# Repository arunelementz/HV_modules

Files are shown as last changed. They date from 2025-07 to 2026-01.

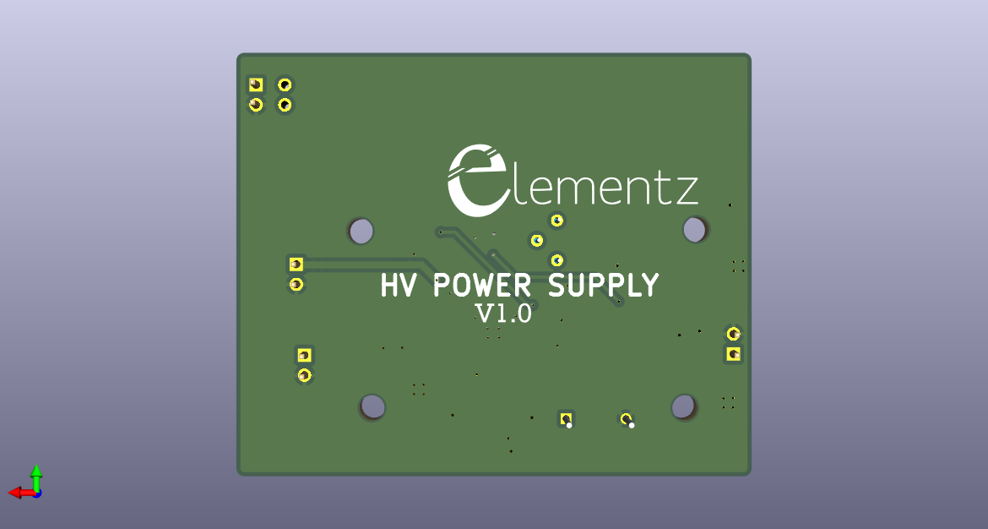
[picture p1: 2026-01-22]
PCB_Design/HV_POWER_SUPPLY_newshape/HV_POWER_SUPPLY_NEWSHAPE_bottom_new.png

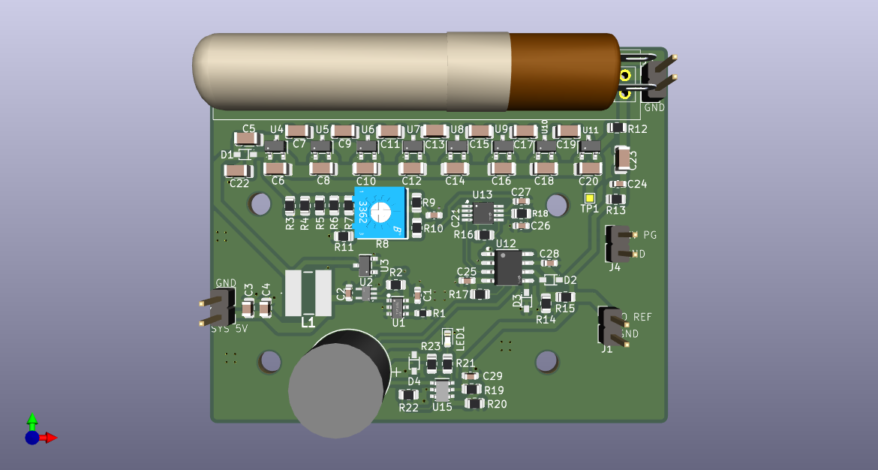
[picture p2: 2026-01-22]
PCB_Design/HV_POWER_SUPPLY_newshape/HV_POWER_SUPPLY_NEWSHAPE_top_new.png

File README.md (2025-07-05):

# HV_Module for GM tubes

## Getting started

To make it easy for you to get started with GitLab, here's a list of recommended next steps.

Already a pro? Just edit this README.md and make it your own. Want to make it easy? [Use the template at the bottom](#editing-this-readme)!

## Add your files

- [ ] [Create](https://docs.gitlab.com/ee/user/project/repository/web_editor.html#create-a-file) or [upload](https://docs.gitlab.com/ee/user/project/repository/web_editor.html#upload-a-file) files
- [ ] [Add files using the command line](https://docs.gitlab.com/topics/git/add_files/#add-files-to-a-git-repository) or push an existing Git repository with the following command:

```
cd existing_repo
git remote add origin https://gitlab.com/arunelementz/hv_module-for-gm-tubes.git
git branch -M main
git push -uf origin main
```

## Integrate with your tools

- [ ] [Set up project integrations](https://gitlab.com/arunelementz/hv_module-for-gm-tubes/-/settings/integrations)

## Collaborate with your team

- [ ] [Invite team members and collaborators](https://docs.gitlab.com/ee/user/project/members/)
- [ ] [Create a new merge request](https://docs.gitlab.com/ee/user/project/merge_requests/creating_merge_requests.html)
- [ ] [Automatically close issues from merge requests](https://docs.gitlab.com/ee/user/project/issues/managing_issues.html#closing-issues-automatically)
- [ ] [Enable merge request approvals](https://docs.gitlab.com/ee/user/project/merge_requests/approvals/)
- [ ] [Set auto-merge](https://docs.gitlab.com/user/project/merge_requests/auto_merge/)

## Test and Deploy

Use the built-in continuous integration in GitLab.

- [ ] [Get started with GitLab CI/CD](https://docs.gitlab.com/ee/ci/quick_start/)
- [ ] [Analyze your code for known vulnerabilities with Static Application Security Testing (SAST)](https://docs.gitlab.com/ee/user/application_security/sast/)
- [ ] [Deploy to Kubernetes, Amazon EC2, or Amazon ECS using Auto Deploy](https://docs.gitlab.com/ee/topics/autodevops/requirements.html)
- [ ] [Use pull-based deployments for improved Kubernetes management](https://docs.gitlab.com/ee/user/clusters/agent/)
- [ ] [Set up protected environments](https://docs.gitlab.com/ee/ci/environments/protected_environments.html)

***

# Editing this README

When you're ready to make this README your own, just edit this file and use the handy template below (or feel free to structure it however you want - this is just a starting point!). Thanks to [makeareadme.com](https://www.makeareadme.com/) for this template.

## Suggestions for a good README

Every project is different, so consider which of these sections apply to yours. The sections used in the template are suggestions for most open source projects. Also keep in mind that while a README can be too long and detailed, too long is better than too short. If you think your README is too long, consider utilizing another form of documentation rather than cutting out information.

## Name
Choose a self-explaining name for your project.

## Description
Let people know what your project can do specifically. Provide context and add a link to any reference visitors might be unfamiliar with. A list of Features or a Background subsection can also be added here. If there are alternatives to your project, this is a good place to list differentiating factors.

## Badges
On some READMEs, you may see small images that convey metadata, such as whether or not all the tests are passing for the project. You can use Shields to add some to your README. Many services also have instructions for adding a badge.

## Visuals
Depending on what you are making, it can be a good idea to include screenshots or even a video (you'll frequently see GIFs rather than actual videos). Tools like ttygif can help, but check out Asciinema for a more sophisticated method.

## Installation
Within a particular ecosystem, there may be a common way of installing things, such as using Yarn, NuGet, or Homebrew. However, consider the possibility that whoever is reading your README is a novice and would like more guidance. Listing specific steps helps remove ambiguity and gets people to using your project as quickly as possible. If it only runs in a specific context like a particular programming language version or operating system or has dependencies that have to be installed manually, also add a Requirements subsection.

## Usage
Use examples liberally, and show the expected output if you can. It's helpful to have inline the smallest example of usage that you can demonstrate, while providing links to more sophisticated examples if they are too long to reasonably include in the README.

## Support
Tell people where they can go to for help. It can be any combination of an issue tracker, a chat room, an email address, etc.

## Roadmap
If you have ideas for releases in the future, it is a good idea to list them in the README.

## Contributing
State if you are open to contributions and what your requirements are for accepting them.

For people who want to make changes to your project, it's helpful to have some documentation on how to get started. Perhaps there is a script that they should run or some environment variables that they need to set. Make these steps explicit. These instructions could also be useful to your future self.

You can also document commands to lint the code or run tests. These steps help to ensure high code quality and reduce the likelihood that the changes inadvertently break something. Having instructions for running tests is especially helpful if it requires external setup, such as starting a Selenium server for testing in a browser.

## Authors and acknowledgment
Show your appreciation to those who have contributed to the project.

## License
For open source projects, say how it is licensed.

## Project status
If you have run out of energy or time for your project, put a note at the top of the README saying that development has slowed down or stopped completely. Someone may choose to fork your project or volunteer to step in as a maintainer or owner, allowing your project to keep going. You can also make an explicit request for maintainers.

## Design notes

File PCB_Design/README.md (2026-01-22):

## HV Schematic and PCB Design Notes

- Schematic is the same as the original **CN0536 board**, including all annotations.
- **Sound notification** is **not included** in the PCB design.
- **BOM** is based on the original **CN0536 BOM**.
- **R19 and R20** are changed to **30 MΩ**  
  - Note: CN0536 BOM specifies **30 MΩ**, but a **different value appears in the schematic** and needs verification.
- **CN0536 stack arrangement** differs and should follow the reference shown.

- **Footprints to be confirmed**:
  - L1  
  - R9  
  - U1  
  - U5
- **Edge cuts** and **high-voltage trace clearance** need to be confirmed.
- **Potentiometer pin numbering** in schematic symbols has been checked.
- **Polygons** are used for drawing copper zones.

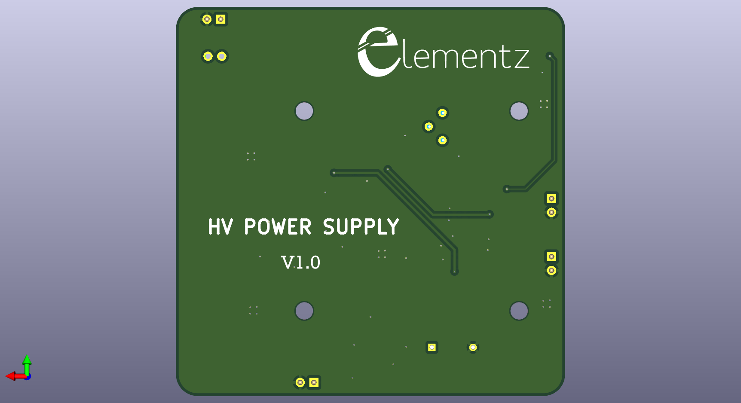
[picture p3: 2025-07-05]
PCB_Design/HV_POWER_SUPPLY_newshape/HV_POWER_SUPPLY_NEWSHAPE_bottom_view.png

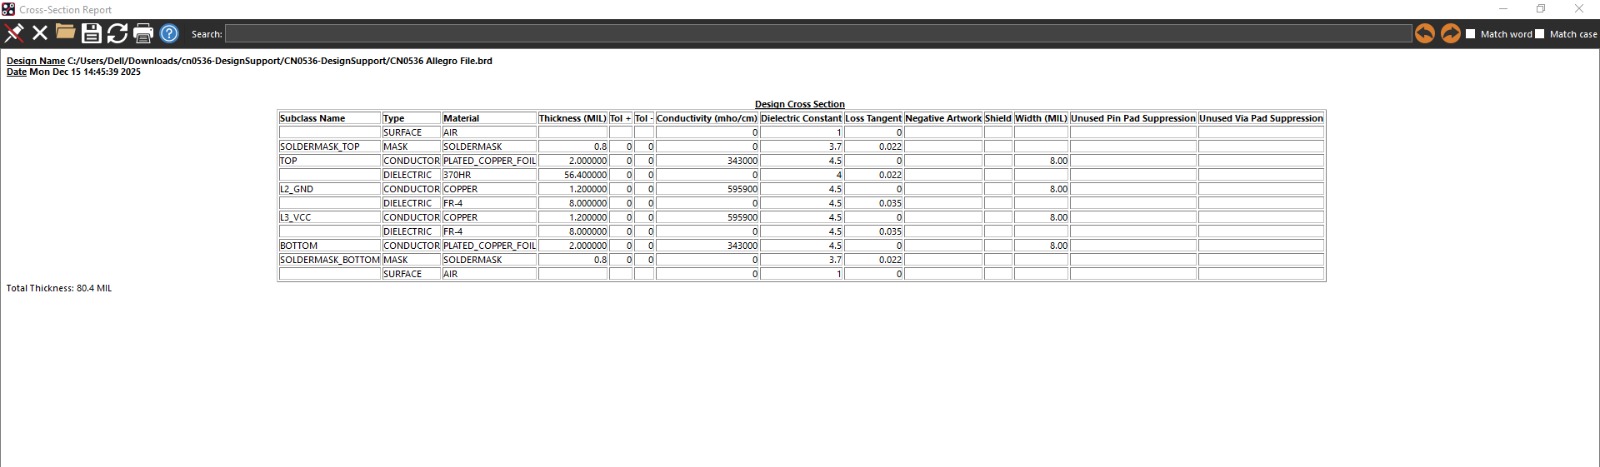
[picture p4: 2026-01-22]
PCB_Design/Stack.png

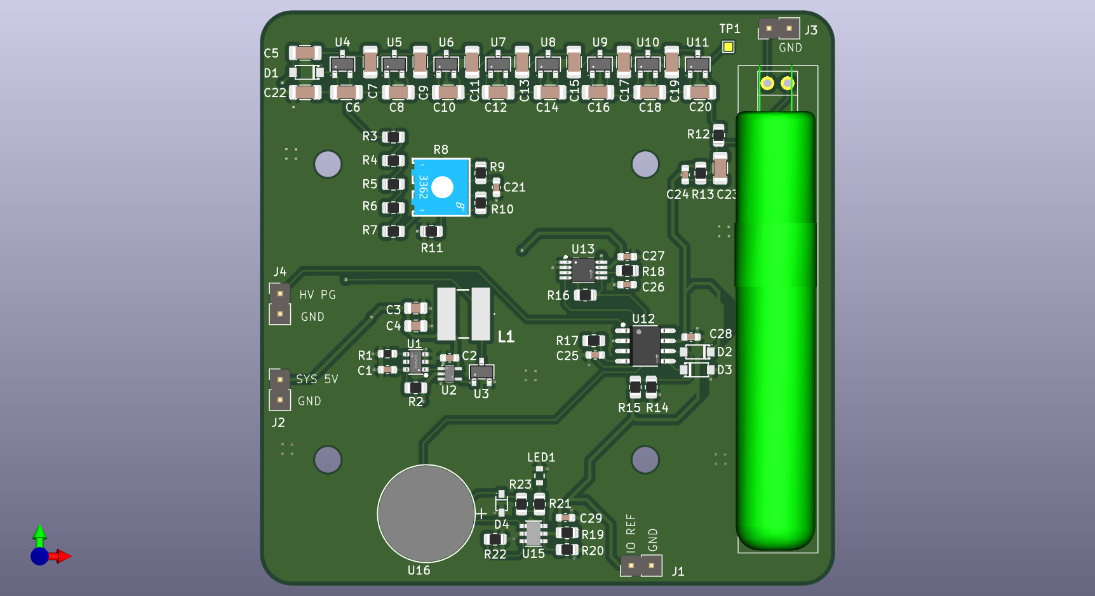
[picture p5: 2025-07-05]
PCB_Design/HV_POWER_SUPPLY_newshape/HV_POWER_SUPPLY_NEWSHAPE_top_view.png

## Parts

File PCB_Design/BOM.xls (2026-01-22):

Item # | *Designator | *Qty | Manufacturer | *Mfg Part # | LCSC | Description / Value | *Package/Footprint | Mounting Type | PCBWay Update
1 | C1,C4,C18,C20,C22,C29 | 6 | AVX | 0603YC105KAT2A | C4153100 | CAP CER 1uF 16V 10% X7R 0603 | 0603 | SMD
2 | C5,C6,C7,C8,C10,C11,C12,C14,C15,C16,C17,C19,C21,C23,C24,C25,C27 | 17 | AVX | 12061C104JAT2A | C597455 | CAP CER 0.1uF 100V 5% X7R 1206 | 1206 | SMD
3 | C9,C13 | 2 | KEMET | C0603C470K5RACAUTO | C2169937 | CAP CER 47pF 50V 10% X7R 0603 AEC-Q200 | 0603 | SMD
4 | C2,C3 | 2 | MURATA | GRM21BR61C106KE15L | C77075 | CAP CER 10uF 16V 10% X5R 0805 | 0805 | SMD
5 | C26 | 1 | MURATA | GRM31A5C2J100JW01D | C162443 | CAP CER 10pF 630V5% C0G/NP0 1206 | 1206 | SMD
6 | C28 | 1 | AVX CORPORATION | 06033A251JAT2A | C2169911 | CAP CER 250pF 25V 5% C0G 0603 | 0603 | SMD
7 | D1,D11,D12 | 3 | DIODES INCORPORATED | BAV21W-7-F | C155214 | DIODE SWITCHING | SOD123-3 | SMD
8 | D2,D3,D4,D5,D6,D7,D8,D9 | 8 | ONSEMI | BAV23S | C151049 | DIO SMALL SIGNAL, 0.2A | SOT23 | SMD
9 | DS1 | 1 | XINGLIGHT | XL-1608SURC-06 | C965799 | LED SMD 0603 RED | 0603 | SMD
10 | L1 | 1 | COILCRAFT | LPS6235-473MRB | C3911705 | IND SHIELDED POWER | LSMSQ236H138 | SMD
11 | JI,J2,J3,J4,J5 | 5 | ADAM TECH | PH1-02-UA | C5828287 | PinHeader_1x02_P2.54mm_Vertical | Plugin,P=2.54mm | Thru-hole
12 | Q2 | 1 | DIODES INCORPORATED | DMN10H220L-7 | C102615 | TRAN N-CH ENHANCEMENT MOSFET, 1.6A | SOT23-M3 | SMD
13 | R1 | 1 | YAGEO | RC0603FR-07287KL | C245944 | RES SMD 287K Ohm 1% 1/10W 0603 | 0603 | SMD
14 | R6,R12,R15 | 3 | MULTICOMP (SPC) | MC0063W06031127K | C2079749 | RES SMD 127K Ohm 1% 1/16W 0603 | 0603 | SMD
15 | R13,R14 | 2 | VISHAY | CRCW0603453KFKEA | C2079749 | RES SMD 453K Ohm 1% 1/10W 0603 AEC-Q200 | 0603 | SMD
16 | R16 | 1 | YAGEO | RC0603FR-071KL | C22548 | RES SMD 1K Ohm 1% 1/10W 0603 | 0603 | SMD
17 | R18 | 1 | PANASONIC | ERJ-3EKF1000V | C193336 | RES SMD 100 Ohm 1% 1/10W 0603 AEC-Q200 | 0603 | SMD
18 | R3,R4,R5,R19,R20 | 5 | STACKPOLE ELECTRONICS, INC. | HVCB0805FDC30M0 | C2641377 | RES SMD 30MEG Ohm 1% 1/5W 0805 HIGH VOLTAGE | 0805 | SMD
19 | R2 | 1 | Ever Ohms Tech | TP0805B221RP0510Z | C5184183 | RES SMD 221 Ohm 0.1% 1/8W 0805 | 0805 | SMD
20 | R21 | 1 | PANASONIC | ERJ-3EKF2003V | C118142 | RES SMD 200K Ohm 1% 1/10W 0603 AEC-Q200 | 0603 | SMD
21 | R7,R27 | 2 | VISHAY | CRCW06033M00FKEA | C4299696 | RES SMD 3MEG Ohm 1% 1/10W 0603 AEC-Q200 | 0603 | SMD
22 | R28 | 1 | YAGEO | RC0603FR-072ML | C114615 | RES SMD 2MEG Ohm 1% 1/10W 0603 | 0603 | SMD
23 | R8 | 1 | PANASONIC | ERJ-3GEYJ275V | C403468 | RES SMD 2.7M OHM 5% 1/10W 0603, AEC-Q200 | 0603 | SMD
24 | R9 | 1 | BOURNS | 3362P-1-205LF | C124582 | RES TH TRIMMER 2MEG Ohm 10% 1/2W 6.6x6.99x4.7mm | POTBOURNS3262P | Thru-hole
25 | U1 | 1 | TEXAS INSTRUMENTS | SN74LVC1G08DCKR | C7832 | IC-TTL SINGLE POSITIVE AND GATE | SC70-5 | SMD
26 | U2 | 1 | ANALOG DEVICES | LTC1540IMS8#PBF | C580397 | IC-ADI NANOPOWER COMPARATOR WITH REFERENCE | MSOP8 | SMD
27 | U3 | 1 | ANALOG DEVICES | LTC6906IS6#TRMPBF | C689638 | IC-ADI MICROPOWER, 10KHZ TO 1MEGHZ RESISTOR SET OSCILLATOR | TSOT23_6 | SMD
28 | U4 | 1 | ANALOG DEVICES | LTC6994CS6-1#TRMPBF | C581050 | IC-ADI TIMERBLOX DELAY CLOCK/DEBOUNCER | TSOT23_6 | SMD
29 | U5 | 1 | ANALOG DEVICES | LTC1441CS8#PBF | C675522 | IC-ADI ULTRALOW POWER DUAL COMPARATOR WITH REFERENCE | SO8NB-5 | SMD
30 | R22 | 1 | UNI-ROYAL(Uniroyal Elec) | 0603WAJ0331T5E | C25231 | RES SMD 330 Ohm 5% 1/10W 0603 AEC-Q200 | 0603 | SMD

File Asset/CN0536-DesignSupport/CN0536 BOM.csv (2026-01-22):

TITLE: Bill of Materials
BOM NO: 05-057494-01-d.csv
DATE: 02/28/2021
DESIGN: 02_057494d_top
TEMPLATE: Z:\allegro\v172_site\cdssetup\template.bom
CALLOUT: C:\tmp\20_057494d\worklib\02_057494d_top\bom\mech.callouts
ITEM# | Qty | WW_PN | DESCRIPTION | VALUE | JEDEC_TYPE | TOL | VOLTAGE | WATTAGE | LOCATION | MFG | MFG_PN | HLM_STATUS | STOCKROOM_WL | STOCKROOM_GT | STOCKROOM_LK | STOCKROOM_GBO | STOCKROOM_NSH | CUSTOM_PART | DNI
1 | 1 | 08_057494d | PCB | ? | ? | ? | ? | ? | ? | Analog Devices Supplied | 08_057494d | N/A | ? | ? | ? | ? | ? | ? | ?
2 | 6 | E020111 | CAP CER 1uF 16V 10% X7R 0603 | 1uF | C0603 | 10 | 16V | N/A | C1,C4,C18,C20,C22,C29 | AVX | 0603YC105KAT2A | REL | N/A | N/A | N/A | N/A | N/A | ? | ?
3 | 17 | E019934 | CAP CER 0.1uF 100V 5% X7R 1206 | 0.1uF | C1206 | 5 | 100V | N/A | C5,C6,C7,C8,C10,C11,C12,C14,C15,C16,C17,C19,C21,C23,C24,C25,C27 | AVX | 12061C104JAT2A | REL | N/A | N/A | N/A | N/A | N/A | ? | ?
4 | 2 | E040135 | CAP CER 47pF 50V 10% X7R 0603 AEC-Q200 | 47pF | C0603 | 10 | 50V | N/A | C9,C13 | KEMET | C0603C470K5RACAUTO | REL | N/A | N/A | N/A | N/A | N/A | ? | ?
5 | 2 | E006166 | CAP CER 10uF 16V 10% X5R 0805 | 10uF | C0805H53 | 10 | 16V | N/A | C2,C3 | MURATA | GRM21BR61C106KE15L | REL | A004-0008-060 | N/A | N/A | 1447_CAB3 | N/A | ? | ?
6 | 1 | E041857 | CAP CER 10pF 630V5% C0G/NP0 1206 | 10pF | C1206H37 | 5 | 630V | N/A | C26 | MURATA | GRM31A5C2J100JW01D | REL | N/A | N/A | N/A | N/A | N/A | ? | ?
7 | 1 | E040628 | CAP CER 250pF 25V 5% C0G 0603 | 250pF | C0603 | 5 | 25V | N/A | C28 | AVX CORPORATION | 06033A251JAT2A | REL | N/A | N/A | N/A | N/A | N/A | ? | ?
8 | 3 | E015087 | DIODE SWITCHING | BAV21W-7-F | SOD123-3 | N/A | 200V | 1/4W | D1,D11,D12 | DIODES INCORPORATED | BAV21W-7-F | REL | N/A | N/A | N/A | N/A | 7003779 | ? | ?
9 | 1 | E001129 | DIODE SWITCHING | BAS16HT1G | SOD323 | N/A | 100V | N/A | D10 | ON SEMICONDUCTOR | BAS16HT1G | REL | A002-0002-050 | N/A | N/A | N/A | 7003752 | ? | ?
10 | 8 | E034937 | DIO SMALL SIGNAL, 0.2A | BAV23S | SOT23 | N/A | 250V | 7/20W | D2,D3,D4,D5,D6,D7,D8,D9 | ONSEMI | BAV23S | REL | N/A | N/A | N/A | N/A | N/A | ? | ?
11 | 4 | E018253 | LED SMD 0603 RED | TLMS1000GS08 | LED0603 | N/A | N/A | N/A | DS1,DS4,DS5,DS6 | VISHAY | TLMS1000-GS08 | REL | N/A | N/A | N/A | N/A | 7004239 | ? | ?
12 | 2 | E026542 | LED BRILLIANT ORANGE 611NM | 19-217/S2C-AL1M2VY/3T | LED0603_A | N/A | 5V | 0.06W | DS2,DS3 | EVERLIGHT AMERICAS INC. | 19-217/S2C-AL1M2VY/3T | REL | N/A | N/A | N/A | N/A | N/A | ? | ?
13 | 1 | E004447 | RES SMD 0 Ohm JUMPER 1/10W 0603 AEC-Q200 | 0 | R0603 | JUMPER | N/A | 1/10W | JP1 | PANASONIC | ERJ-3GEY0R00V | REL | N/A | N/A | N/A | N/A | 7008623 | ? | ?
15 | 1 | E018439 | IND SHIELDED POWER | 47uH | LSMSQ236H138 | 20 | N/A | N/A | L1 | COILCRAFT | LPS6235-473MRB | REL | N/A | N/A | N/A | N/A | 7005247 | ? | ?
16 | 1 | E030982 | IC MAGNETIC BUZZER INDICATOR | AI-1223-TWT-5V-5-R | TORAD299D472H382 | N/A | N/A | ? | M1 | PUI AUDIO, INC. | AI-1223-TWT-5V-5-R | REL | N/A | N/A | N/A | N/A | N/A | ? | ?
17 | 1 | E039719 | MOD SENSITIVE SMALL GEIGER MULLER TUBE G-M 1X M044026 | SI-29BG | MSI-29BG | N/A | N/A | N/A | M2 | N/A | SI-29BG | REL | N/A | N/A | N/A | N/A | N/A | ? | ?
18 | 2 | E020478 | CONN-PCB RCPT 25MIL SQ POST 2.54MM P | SSQ-108-03-G-S | CNSAMTECSSQ-108-XX-X-S | N/A | N/A | N/A | P1,P4 | SAMTEC | SSQ-108-03-G-S | REL | N/A | N/A | N/A | N/A | N/A | ? | ?
19 | 1 | E020477 | CONN-PCB RCPT 25MIL SQ POST 2.54MM PITCH | SSQ-106-03-G-S | CNSAMTECSSQ-106-XX-X-S | N/A | N/A | N/A | P2 | SAMTEC | SSQ-106-03-G-S | REL | N/A | N/A | N/A | N/A | N/A | ? | ?
20 | 1 | E020479 | CONN-PCB RCPT 25MIL SQ POST 2.54MM PITCH | SSQ-110-03-G-S | CNSAMTECSSQ-110-XX-X-S | N/A | N/A | N/A | P3 | SAMTEC | SSQ-110-03-G-S | REL | N/A | N/A | N/A | N/A | N/A | ? | ?
21 | 1 | E006296 | CONN-PCB HEADER 2 POS | TSW-102-08-G-S | CNSAMTEC1X2H330LD36 | N/A | N/A | N/A | P5 | SAMTEC | TSW-102-08-G-S | REL | ADD_TO_STOCK_2 | N/A | N/A | N/A | N/A | ? | ?
22 | 4 | E025627 | TRAN NPN SILICON | MMBT3904LT3G | SOT23 | N/A | 40V | N/A | Q1,Q3,Q4,Q5 | ONSEMI | MMBT3904LT3G | REL | N/A | N/A | N/A | N/A | N/A | ? | ?
23 | 1 | E042109 | TRAN N-CH ENHANCEMENT MOSFET, 1.6A | DMN10H220L-7 | SOT23-M3 | N/A | 100V | N/A | Q2 | DIODES INCORPORATED | DMN10H220L-7 | REL | N/A | N/A | N/A | N/A | N/A | ? | ?
24 | 1 | E026586 | RES SMD 287K Ohm 1% 1/10W 0603 | 287K | R0603 | 1 | N/A | 1/10W | R1 | YAGEO | RC0603FR-07287KL | REL | N/A | N/A | N/A | N/A | N/A | ? | ?
26 | 3 | E025582 | RES SMD 127K Ohm 1% 1/16W 0603 | 127K | R0603 | 1 | N/A | 1/16W | R6,R12,R15 | MULTICOMP (SPC) | MC0063W06031127K | REL | N/A | N/A | N/A | N/A | N/A | ? | ?
27 | 2 | E032192 | RES SMD 453K Ohm 1% 1/10W 0603 AEC-Q200 | 453K | R0603 | 1 | N/A | 1/10W | R13,R14 | VISHAY | CRCW0603453KFKEA | REL | N/A | N/A | N/A | N/A | N/A | ? | ?
28 | 1 | E029591 | RES SMD 1K Ohm 1% 1/10W 0603 | 1K | R0603 | 1 | N/A | 1/10W | R16 | YAGEO | RC0603FR-071KL | REL | N/A | N/A | N/A | N/A | N/A | ? | ?
29 | 6 | E003857 | RES SMD 330 Ohm 5% 1/10W 0603 AEC-Q200 | 330 | R0603 | 5 | N/A | 1/10W | R17,R22,R23,R24,R25,R26 | PANASONIC | ERJ-3GEYJ331V | REL | N/A | N/A | N/A | N/A | N/A | ? | ?
30 | 1 | E003668 | RES SMD 100 Ohm 1% 1/10W 0603 AEC-Q200 | 100 | R0603 | 1 | N/A | 1/10W | R18 | PANASONIC | ERJ-3EKF1000V | REL | A003-0032-003 | 41816DG308 | FEC 911-112 | 1514_CAB3 | 7005700 | ? | ?
31 | 5 | E034828 | RES SMD 30MEG Ohm 1% 1/5W 0805 HIGH VOLTAGE | 30MEG | R0805 | 1 | N/A | 1/5W | R3,R4,R5,R19,R20 | STACKPOLE ELECTRONICS, INC. | HVCB0805FDC30M0 | REL | N/A | N/A | N/A | N/A | N/A | ? | ?
32 | 1 | E004167 | RES SMD 221 Ohm 0.1% 1/10W 0805 | 221 | R0805 | 0.1 | N/A | 1/10W | R2 | MEGGIT | RN73C2A221RBTG | REL | ADD_TO_STOCK_112 | 41816DG1235 | FEC 553-372 | N/A | 7006822 | ? | ?
33 | 1 | E015343 | RES SMD 200K Ohm 1% 1/10W 0603 AEC-Q200 | 200K | R0603 | 1 | N/A | 1/10W | R21 | PANASONIC | ERJ-3EKF2003V | REL | N/A | N/A | N/A | N/A | N/A | ? | ?
34 | 2 | E011856 | RES SMD 3MEG Ohm 1% 1/10W 0603 AEC-Q200 | 3MEG | R0603 | 1 | N/A | 1/10W | R7,R27 | VISHAY | CRCW06033M00FKEA | REL | N/A | N/A | N/A | N/A | 7007465 | ? | ?
35 | 1 | E021609 | RES SMD 2MEG Ohm 1% 1/10W 0603 | 2MEG | R0603 | 1 | N/A | 1/10W | R28 | YAGEO | RC0603FR-072ML | REL | N/A | N/A | N/A | N/A | N/A | ? | ?
36 | 4 | E036086 | RES SMD 3.3K Ohm 5% 1/4W 0603 AEC-Q200 | 3.3K | R0603 | 5 | N/A | 1/4W | R29,R30,R31,R32 | ROHM | ESR03EZPJ332 | REL | N/A | N/A | N/A | N/A | N/A | ? | ?
37 | 1 | E043637 | RES SMD 2.7M OHM 5% 1/10W 0603, AEC-Q200 | 2.7MEG | R0603 | 5 | N/A | 1/10W | R8 | PANASONIC | ERJ-3GEYJ275V | REL | N/A | N/A | N/A | N/A | N/A | ? | ?
38 | 1 | E038798 | RES TH TRIMMER 2MEG Ohm 10% 1/2W 6.6x6.99x4.7mm | 2MEG | POTBOURNS3262P | 10 | N/A | 1/2W | R9 | BOURNS | 3362P-1-205LF | REL | N/A | N/A | N/A | N/A | N/A | ? | ?
39 | 1 | E026439 | SWITCH COMPACT SIZE TALL HEIGHT 0.5A, SPST-NO | SKQMBBE010 | SWSML236W138H197 | N/A | 12V | N/A | S1 | ALPS ELECTRIC INC | SKQMBBE010 | REL | N/A | N/A | N/A | N/A | N/A | ? | ?
40 | 1 | E019772 | IC-TTL SINGLE POSITIVE AND GATE | SN74LVC1G08DCKR | SC70-5 | N/A | N/A | ? | U1 | TEXAS INSTRUMENTS | SN74LVC1G08DCKR | REL | N/A | N/A | N/A | N/A | N/A | ? | ?
41 | 1 | E043510 | IC-ADI NANOPOWER COMPARATOR WITH REFERENCE | LTC1540IMS8#PBF | MSOP8 | N/A | N/A | ? | U2 | ANALOG DEVICES | LTC1540IMS8#PBF | REL | N/A | N/A | N/A | N/A | N/A | ? | ?
42 | 1 | E038452 | IC-ADI MICROPOWER, 10KHZ TO 1MEGHZ RESISTOR SET OSCILLATOR | LTC6906IS6#PBF | TSOT23_6 | N/A | N/A | ? | U3 | ANALOG DEVICES | LTC6906IS6#PBF | REL | N/A | N/A | N/A | N/A | N/A | ? | ?
43 | 1 | E038792 | IC-ADI TIMERBLOX DELAY CLOCK/DEBOUNCER | LTC6994CS6-1#TRMPBF | TSOT23_6 | N/A | N/A | ? | U4 | ANALOG DEVICES | LTC6994CS6-1#TRMPBF | REL | N/A | N/A | N/A | N/A | N/A | ? | ?
44 | 1 | E038786 | IC-ADI ULTRALOW POWER DUAL COMPARATOR WITH REFERENCE | LTC1441CS8#PBF | SO8NB-5 | N/A | N/A | ? | U5 | ANALOG DEVICES | LTC1441CS8#PBF | REL | N/A | N/A | N/A | N/A | N/A | ? | ?
Callouts File:C:\tmp\20_057494d\worklib\02_057494d_top\bom\mech.callouts
Mechanical Parts
ITEM# | Qty | WW_PN | DESCRIPTION | VALUE | JEDEC_TYPE | TOL | VOLTAGE | WATTAGE | LOCATION | MFG | MFG_PN | HLM_STATUS | STOCKROOM_WL | STOCKROOM_GT | STOCKROOM_LK | STOCKROOM_GBO | STOCKROOM_NSH | CUSTOM_PART | DNI
2 | 1 | M044026 | CONNECTOR HEADER VERT 2POS 2.54MM | ? | N/A | ? | ? | ? | ? | SAMTEC INC. | TSW-102-09-G-S | REL | N/A | N/A | N/A | N/A | N/A | ? | ?
3 | 1 | M036050 | SHUNT 2 (2X1) POS CONNECTOR BLACK 2.54MM | ? | N/A | ? | ? | ? | ? | SAMTEC INC. | SNT-100-BK-T | REL | N/A | N/A | N/A | N/A | N/A | ? | ?
4 | 2 | M044354 | CABLE TIE LOCKING BLACK 18LBS 104.24MM LONG | ? | N/A | ? | ? | ? | ? | 3M | CT4BK18-C | REL | N/A | N/A | N/A | N/A | N/A | ? | ?
The following components are part of the PCB or are NOT to be installed
ITEM# | Qty | WW_PN | DESCRIPTION | VALUE | JEDEC_TYPE | TOL | VOLTAGE | WATTAGE | LOCATION | MFG | MFG_PN | HLM_STATUS | STOCKROOM_WL | STOCKROOM_GT | STOCKROOM_LK | STOCKROOM_GBO | STOCKROOM_NSH | CUSTOM_PART | DNI
14 | 3 | E004447 | RES SMD 0 Ohm JUMPER 1/10W 0603 AEC-Q200 | 0 | R0603 | JUMPER | N/A | 1/10W | JP2,JP3,JP4 | PANASONIC | ERJ-3GEY0R00V | REL | N/A | N/A | N/A | N/A | 7008623 | ? | DNI
25 | 2 | E003682 | RES SMD 1MEG Ohm 1% 1/10W 0603 AEC-Q200 | 1MEG | R0603 | 1 | N/A | 1/10W | R10,R11 | PANASONIC | ERJ-3EKF1004V | REL | A003-0032-017 | 41816DG307 | FEC 911-598 | N/A | N/A | ? | DNI

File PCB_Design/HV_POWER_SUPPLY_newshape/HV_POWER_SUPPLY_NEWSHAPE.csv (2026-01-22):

Reference | Value | Footprint | Qty | DNP | LCSC | Description | Manufacturer | manufacturer Part Number | Package | Digikey part number | Elements14
C1,C4,C18,C20,C22,C29 | 1uF | Capacitor_SMD:C_0603_1608Metric | 6 |  | C4153100 | 16V 1uF X7R ±10% 0603 | AVX | 0603YC105KAT2A | 0603
C2,C3 | 10uF | Capacitor_SMD:C_0805_2012Metric | 2 |  | C77075 | 10uF 16V X5R ±10% 0805 | Murata Electronics | GRM21BR61C106KE15L | 0805
C5,C6,C7,C8,C10,C11,C12,C14,C15,C16,C17,C19,C21,C23,C24,C25,C27 | 0.1uF | Capacitor_SMD:C_1206_3216Metric | 17 |  | C597455 | 100V 100nF X7R ±10% 1206 | AVX | 12061C104JAT2A | 1206
C9,C13 | 47pF | Capacitor_SMD:C_0603_1608Metric | 2 |  | C2169937 | 47pF 50V X7R ±10% 0603 | KEMET | C0603C470K5RACAUTO | 0603
C26 | 10pF | Capacitor_SMD:C_1206_3216Metric | 1 |  | C22374878 | 10pF 1kV C0G ±5% 1206 | HRE | CGA1206C0G100J102MT | 1206
C28 | 250pF | Capacitor_SMD:C_0603_1608Metric | 1 |  | C2169911 | 250pF 25V C0G ±5% 0603 | AVX CORPORATION | 06033A251JAT2A | 0603 | 478-11806-2-ND
D1,D11,D12 | BAV21W-7-F | HV_POWER_SUPPLY:SOD-123_L2.8-W1.8-LS3.7-RD | 3 |  | C155214 | 1.25V@200mA 200V 200mA 250mW 50ns SOD-123 Switching Diodes | Diodes Incorporated | BAV21WS-7-F | SOD-323
D2,D3,D4,D5,D6,D7,D8,D9 | BAV23S | HV_POWER_SUPPLY:BAV23S_SOT-23-3_L2.9-W1.6-P1.90-LS2.8-BR | 8 |  | C151049 | .25V@200mA 100nA@200V 200V 350mW 400mA 50ns SOT-23 Switching Diodes | Diodes Incorporated | BAV23S | SOT-23
DS1 | TLMS1000-GS08 | LED_SMD:LED_0603_1608Metric | 1 |  | C2286 | ed Water Clear 0603 LED | Hubei KENTO Elec | KT-0603R | 0603
J1,J2,J3,J4,J5 | Conn_01x02 | Connector_PinHeader_2.54mm:PinHeader_1x02_P2.54mm_Vertical | 5 |  | C5828287 | P=2.54mm Pin Headers | ADAM TECH | PH1-02-UA | Plugin,P=2.54mm
L1 | LPS6235-473MRB | HV_POWER_SUPPLY:LPS6235473MRB | 1 |  | C3911705 | Magnetic Shielded Inductor ±20% SMD | C3911705 | LPS6235-473MRC | SMD,6.2x6.2mm |  | LPS6235-473MRB
Q2 | DMN10H220L-7 | HV_POWER_SUPPLY:SOT-23-3_L2.9-W1.6-P1.90-LS2.8-BR | 1 |  | C102615 | 250mΩ@4.5V 401pF 8.3nC@10V N-Channel SOT-23 MOSFETs | Diodes Incorporated | DMN10H220L-7 | SOT-23
R1 | 287K | Resistor_SMD:R_0603_1608Metric | 1 |  | C245944 | 100mW 287kΩ 75V Thick Film Resistor ±1% ±100ppm/℃ 0603 | YAGEO | RC0603FR-07287KL | 0603
R2 | 221 | Resistor_SMD:R_0805_2012Metric | 1 |  | C5184183 | 221Ω Thin Film Resistor ±0.1% ±10ppm/℃ 0805 125mW 150V | Ever Ohms Tech | TP0805B221RP0510Z | 0805
R3,R4,R5,R19,R20 | 30Meg | Resistor_SMD:R_0805_2012Metric | 5 |  | HVCB0805FDC30M0 | 30MΩ 600V Thick Film Resistor ±1% ±50ppm/℃ 0805 200mW | SEI(Stackpole Elec) | HVCB0805FDC30M0 | 0805
R6,R12,R15 | 127K | Resistor_SMD:R_0603_1608Metric | 3 |  | C245905 | 127kΩ 75V Thick Film Resistor ±1% ±100ppm/℃ 0603 | YAGEO | RC0603FR-07127KL | 0603
R7,R27 | 3Meg | Resistor_SMD:R_0603_1608Metric | 2 |  | C4299696 | 3MΩ Thick Film Resistor ±1% ±100ppm/℃ 0603 100mW | Vishay Intertech | CRCW06033M00FKEA | 0603
R8 | 2.7Meg | Resistor_SMD:R_0603_1608Metric | 1 |  | C403468 | 2.7MΩ Thick Film Resistor ±5% 0603 100mW 150V | PANASONIC | FRC0805F2704TS | 0603
R9 | 3362P-1-205LF | HV_POWER_SUPPLY:RES-ADJ-TH_3362P | 1 |  | C124582 | 1 2MΩ 500mW ±10% ±100ppm/℃ Plugin-3P,7x6.6mm Potentiometers | BOURNS | 3362P-1-205LF | Plugin-3P,7x6.6mm
R13,R14 | 453K | Resistor_SMD:R_0603_1608Metric | 2 |  | C273765 | 453kΩ 75V Thick Film Resistor ±1% ±100ppm/℃ 0603 100mW | YAGEO | RC0603FR-07453KL | 0603
R16 | 1K | Resistor_SMD:R_0603_1608Metric | 1 |  | C22548 | 1kΩ 75V Thick Film Resistor ±1% ±100ppm/℃ 0603 100mW | YAGEO | RC0603FR-071KL | 0605
R21 | 200K | Resistor_SMD:R_0603_1608Metric | 1 |  | C118142 | 200kΩ Thick Film Resistor ±1% ±100ppm/℃ 0603 | PANASONIC | ERJ3EKF2003V | 0603
R22 | 330 | Resistor_SMD:R_0603_1608Metric | 1 |  | C25231 | 330Ω 75V Thick Film Resistor ±100ppm/℃ ±5% 0603 100mW | UNI-ROYAL | 0603WAJ0331T5E | 0603
R28 | 2Meg | Resistor_SMD:R_0603_1608Metric | 1 |  | C114615 | 2MΩ 75V Thick Film Resistor ±1% ±100ppm/℃ 0603 | YAGEO | RC0603FR-072ML | 0603
TP1 | TestPoint | TestPoint:TestPoint_Pad_1.0x1.0mm | 1 |  |  | test point
U1 | SN74LVC1G08DCKR_C5279048 | HV_POWER_SUPPLY:SC-70-5_L2.0-W1.3-P0.65-LS2.1-BR | 1 |  | C7832 | 800mV 74LVC Series AND Gate SC-70-5 | Texas Instruments | SN74LVC1G08DCKR | SC-70-5
U2 | LTC1540IMS8#PBF | HV_POWER_SUPPLY:MSOP-8_L3.0-W3.0-P0.65-LS4.9-BL | 1 |  | C580397 | 300nA 50mV 60us TTL、CMOS MSOP-8 Comparators | Analog Devices | LTC1540IMS8#PBF | MSOP-8 | LTC1540IMS8#PBF-ND
U3 | LTC6906IS6#TRPBF | HV_POWER_SUPPLY:TSOT-23-6_L2.9-W1.6-P0.95-LS2.8-BR | 1 |  | C581017 | 2.25V~3.6V 78uA TSOT-23-6L Programmable Oscillators | Analog Devices | LTC6906IS6#TRMPBF | TSOT-23-6 | LTC6906IS6#TRPBFTR-ND
U4 | LTC6994CS6-1-TRMPBF | HV_POWER_SUPPLY:TSOT-23_S6_LIT | 1 |  | C581050 | 2.25V~5.5V TSOT-23-6 Time Delays ROHS | Analog Devices | LTC6994CS6-1#TRMPBF | TSOT-23-6
U5 | LTC1441CS8#PBF | HV_POWER_SUPPLY:SOIC-8_L4.9-W3.8-P1.27-LS6.0-BL | 1 |  | C675522 | 10mV TTL、CMOS SOIC-8 Comparators | Analog Devices | LTC1441CS8#PBF | SOIC-8 | LTC1441CS8#PBF-ND

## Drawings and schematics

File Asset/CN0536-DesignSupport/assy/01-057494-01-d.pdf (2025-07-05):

D

1

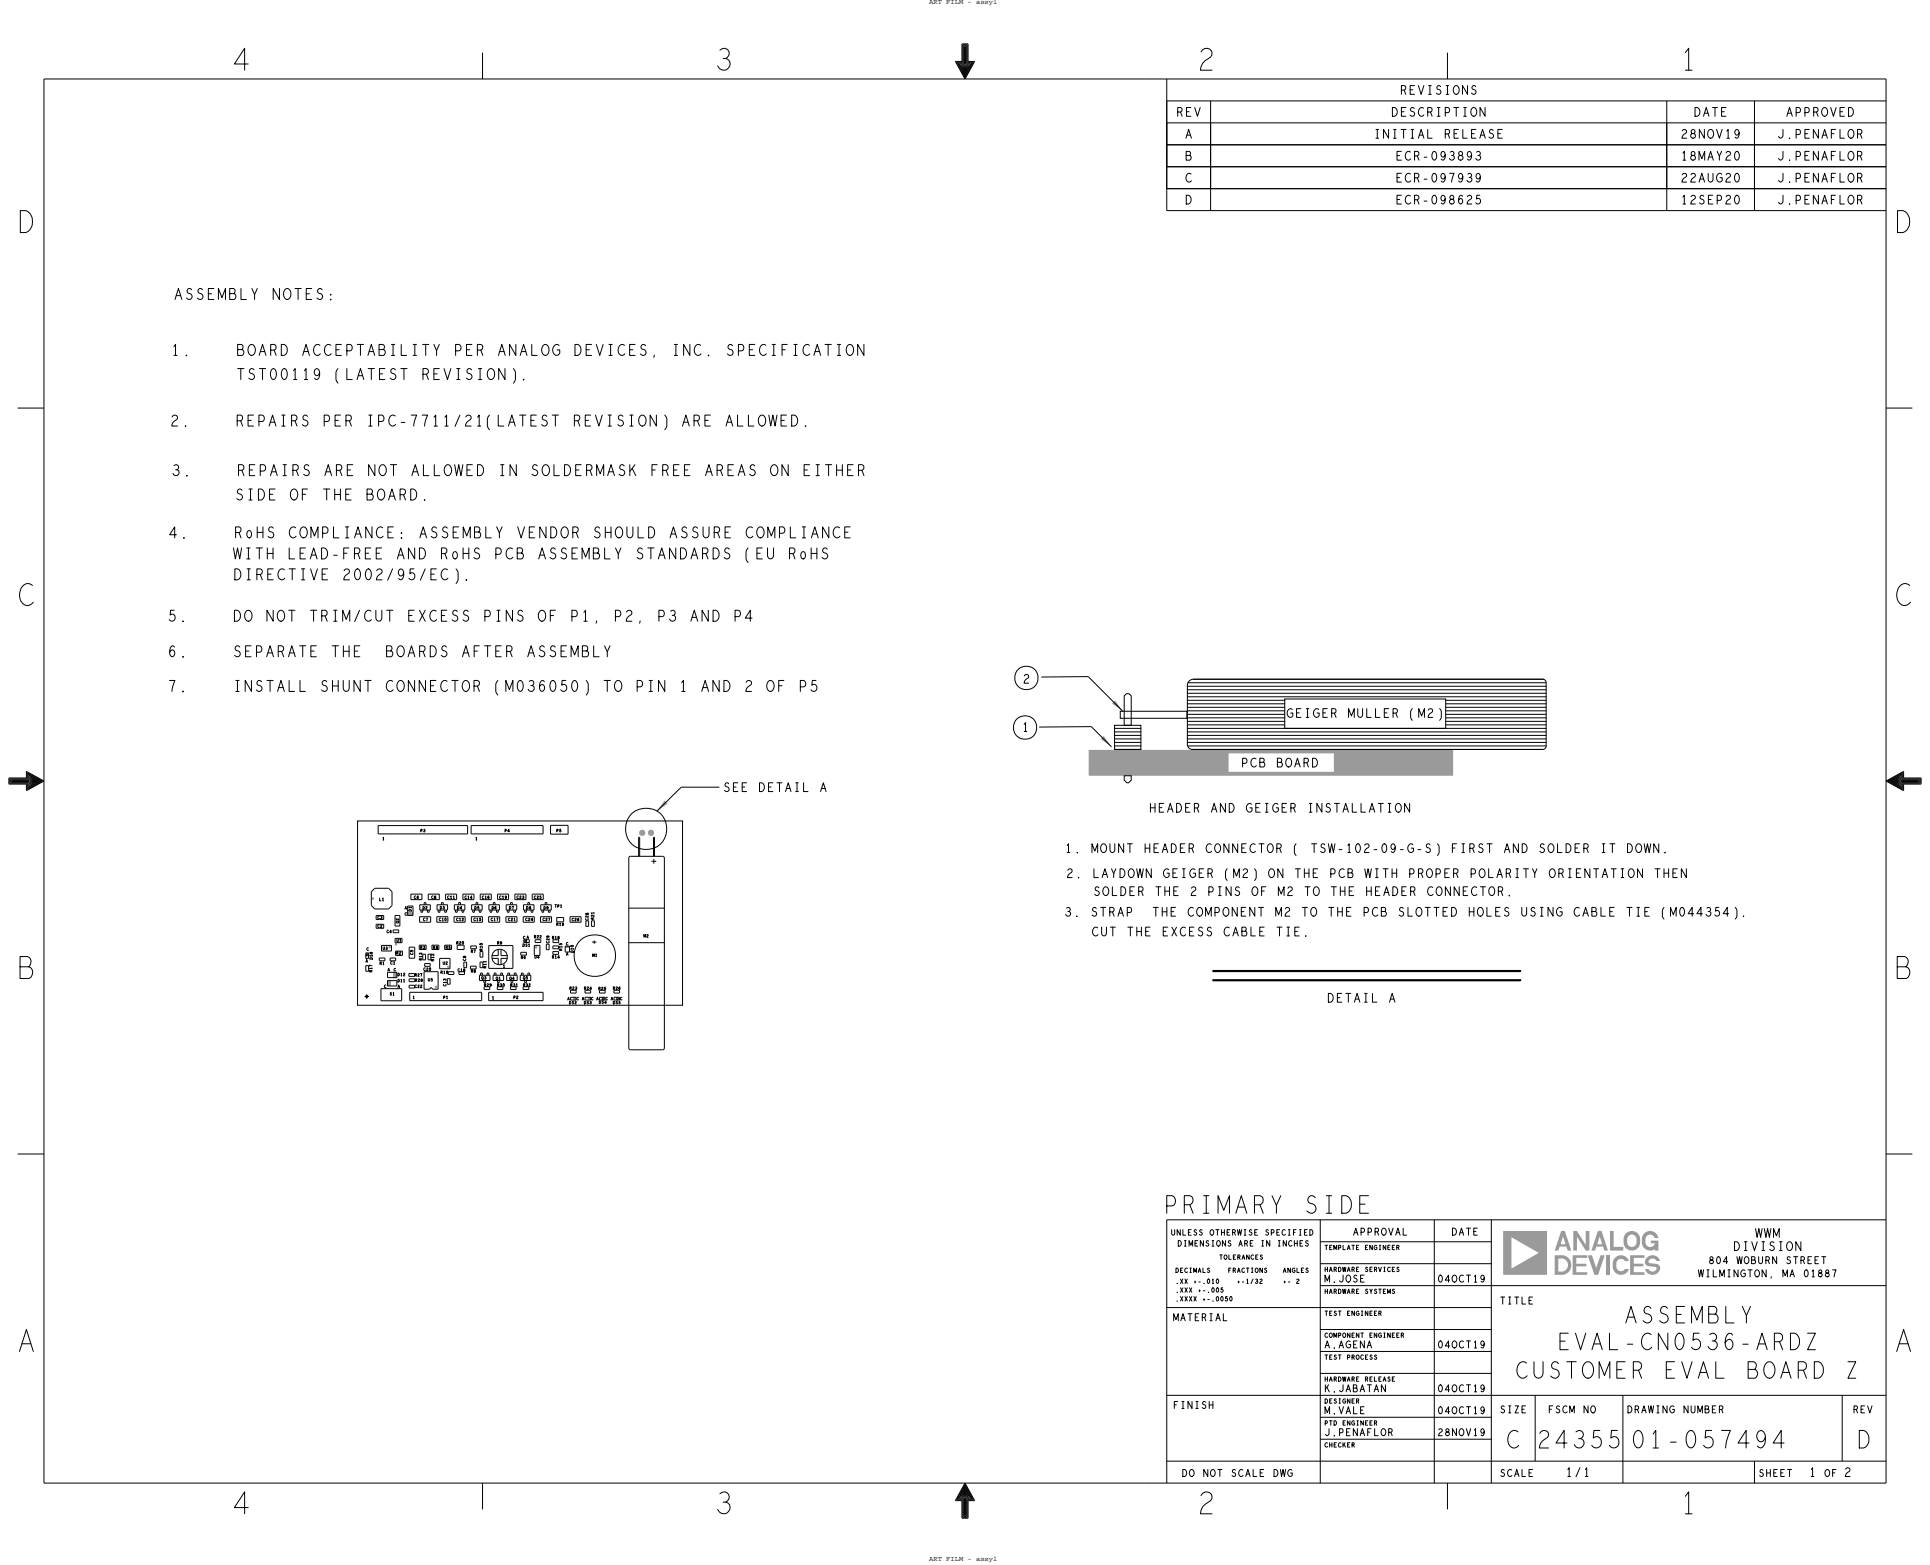
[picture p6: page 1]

REVISIONS

REV | DESCRIPTION | DATE | | APPROVED
A | INITIAL RELEASE | | 28NOV19 | J.PENAFLOR
B | ECR-093893 | | 18MAY20 | J.PENAFLOR
C | ECR-097939 | | 22AUG20 | J.PENAFLOR
D | ECR-098625 | | 12SEP20 | J.PENAFLOR

SIDE OF THE BOARD.

4. RoHS COMPLIANCE: ASSEMBLY VENDOR SHOULD ASSURE COMPLIANCE

WITH LEAD-FREE AND RoHS PCB ASSEMBLY STANDARDS (EU RoHS
DIRECTIVE 2002/95/EC).

5. DO NOT TRIM/CUT EXCESS PINS OF P1, P2, P3 AND P4
6. SEPARATE THE BOARDS AFTER ASSEMBLY

HEADER AND GEIGER INSTALLATION

CUT THE EXCESS CABLE TIE.

UNLESS OTHERWISE SPECIFIED DECIMALS .XX +-.010 .XXX +-.005 .XXXX +-.0050 | TOLERANCES FRACTIONS +-1/32 | | | ANGLES +- | 2 | APPROVAL | DATE

TEMPLATE ENGINEER
HARDWARE SERVICES M.JOSE | 04OCT19
HARDWARE SYSTEMS | | | TITLE ASSEMBLY EVAL-CN0536-ARDZ CUSTOMER EVAL BOARD Z

MATERIAL | | TEST ENGINEER

COMPONENT ENGINEER A.AGENA | 04OCT19

TEST PROCESS
HARDWARE RELEASE | 04OCT19
DESIGNER M.VALE | 04OCT19 | SIZE C | | FSCM NO 24355 | DRAWING NUMBER 01 | -057494 | REV D
PTD ENGINEER J.PENAFLOR | 28NOV19

CHECKER

DO NOT SCALE DWG | | | 1/1 SCALE | | SHEET

D

4

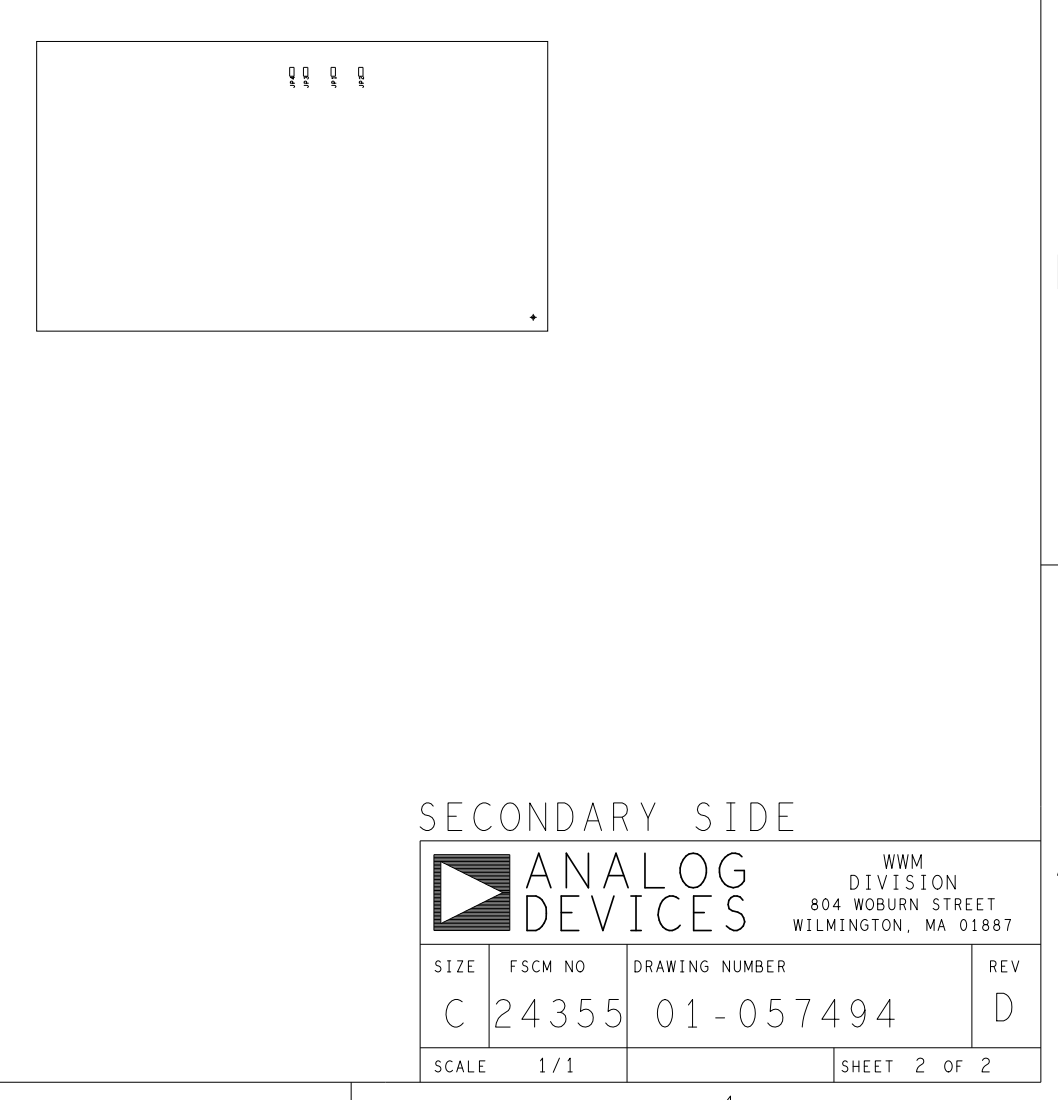
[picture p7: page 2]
ART FILM - assy2; SECONDARY SIDE; WWM; DIVISION; 804 WOBURN STREET WILMINGTON, MA 01887

SIZE C | FSCM NO 24355 | DRAWING NUMBER 01-057494 | REV D

SCALE 1/1 | | SHEET

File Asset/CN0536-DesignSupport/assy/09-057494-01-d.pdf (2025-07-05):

D

1

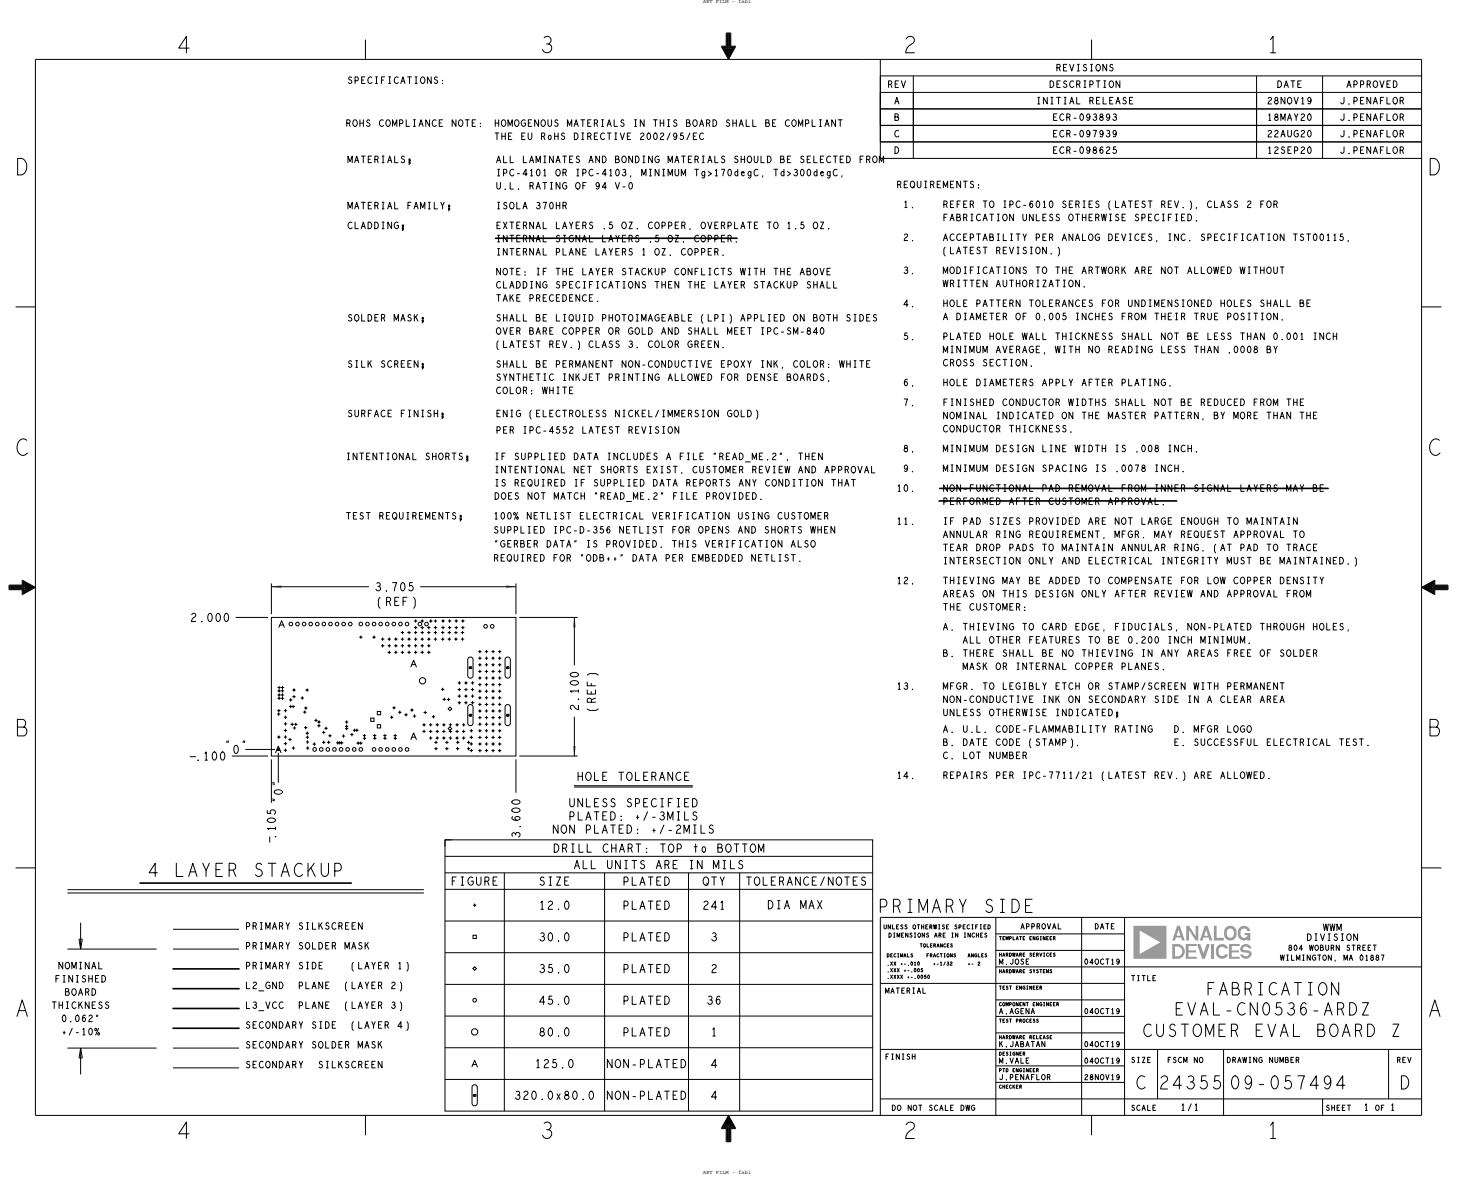
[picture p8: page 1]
ART FILM - fab1; J.PENAFLOR; WWM DIVISION; WILMINGTON, MA 01887; 804 WOBURN STREET; 18MAY20; 12SEP20; 22AUG20; ECR-093893; ECR-098625; ECR-097939; K.JABATAN; REQUIREMENTS:; REFER TO; IPC-6010 SERIES (LATEST REV.), CLASS 2 FOR; ACCEPTABILITY PER ANALOG DEVICES,; INC. SPECIFICATION; TST00115,; (LATEST REVISION.); MODIFICATIONS; THE ARTWORK ARE NOT ALLOWED WITHOUT; WRITTEN AUTHORIZATION.; HOLE PATTERN; TOLERANCES FOR UNDIMENSIONED; HOLES SHALL BE; A DIAMETER OF 0.005; INCHES FROM; THEIR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

REVISIONS

REV | DESCRIPTION | DATE | | APPROVED
A | INITIAL RELEASE | | 28NOV19 | J.PENAFLOR

ROHS COMPLIANCE NOTE:

THE EU RoHS DIRECTIVE 2002/95/EC

ALL LAMINATES AND BONDING MATERIALS SHOULD BE SELECTED FROM
U.L. RATING OF 94 V-0
ISOLA 370HR
INTERNAL SIGNAL LAYERS .5 OZ. COPPER.
INTERNAL PLANE LAYERS 1 OZ. COPPER.
TAKE PRECEDENCE.
SHALL BE LIQUID PHOTOIMAGEABLE (LPI) APPLIED ON BOTH SIDES
(LATEST REV.) CLASS 3. COLOR GREEN.
SYNTHETIC INKJET PRINTING ALLOWED FOR DENSE BOARDS,
COLOR: WHITE

FABRICATION UNLESS OTHERWISE SPECIFIED.

6. HOLE DIAMETERS APPLY AFTER PLATING.

ENIG (ELECTROLESS NICKEL/IMMERSION GOLD)
PER IPC-4552 LATEST REVISION

INTENTIONAL NET SHORTS EXIST. CUSTOMER REVIEW AND APPROVAL
DOES NOT MATCH "READ_ME.2" FILE PROVIDED.
100% NETLIST ELECTRICAL VERIFICATION USING CUSTOMER
SUPPLIED IPC-D-356 NETLIST FOR OPENS AND SHORTS WHEN
REQUIRED FOR "ODB++" DATA PER EMBEDDED NETLIST.

PERFORMED AFTER CUSTOMER APPROVAL.

THE CUSTOMER:
MASK OR INTERNAL COPPER PLANES.

ALL UNITS ARE IN MILS ².100

13. MFGR. TO LEGIBLY ETCH OR STAMP/SCREEN WITH PERMANENT

UNLESS OTHERWISE INDICATED;
C. LOT NUMBER

HOLE TOLERANCE
UNLESS SPECIFIED
PLATED: +/-3MILS
NON PLATED: +/-2MILS
DRILL CHART: TOP to BOTTOM

PRIMARY SILKSCREEN
PRIMARY SOLDER MASK
L2_GND PLANE (LAYER 2)
L3_VCC PLANE (LAYER 3)
SECONDARY SIDE (LAYER 4)
SECONDARY SOLDER MASK
SECONDARY SILKSCREEN

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

TEMPLATE ENGINEER
HARDWARE SERVICES M.JOSE | 04OCT19
HARDWARE SYSTEMS | | | TITLE FABRICATION EVAL-CN0536-ARDZ CUSTOMER EVAL BOARD Z

MATERIAL | | TEST ENGINEER

COMPONENT ENGINEER A.AGENA | 04OCT19

TEST PROCESS
HARDWARE RELEASE | 04OCT19
DESIGNER M.VALE | 04OCT19 | SIZE C | | FSCM NO 24355 | DRAWING NUMBER 09 | -057494 | REV D
PTD ENGINEER J.PENAFLOR | 28NOV19

CHECKER

DO NOT SCALE DWG | | | 1/1 SCALE | | SHEET

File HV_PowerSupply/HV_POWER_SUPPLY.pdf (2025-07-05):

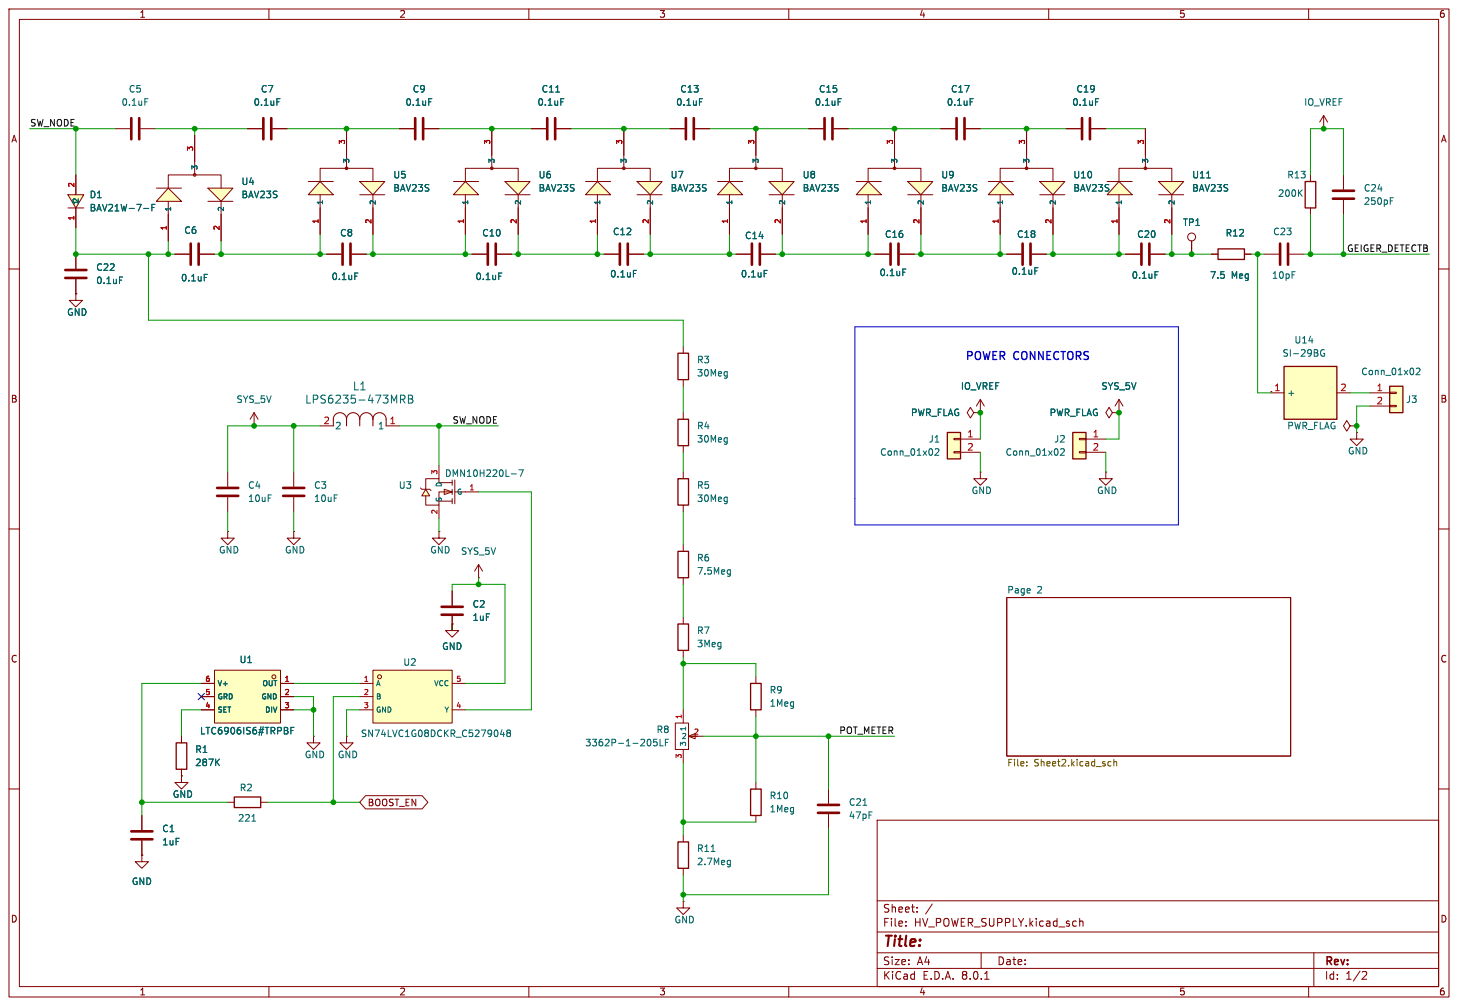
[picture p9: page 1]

LTC6906IS6#TRPBF OUT 1 GND 2 DIV 3 SET 4 GRD 5 V+ 6 R1

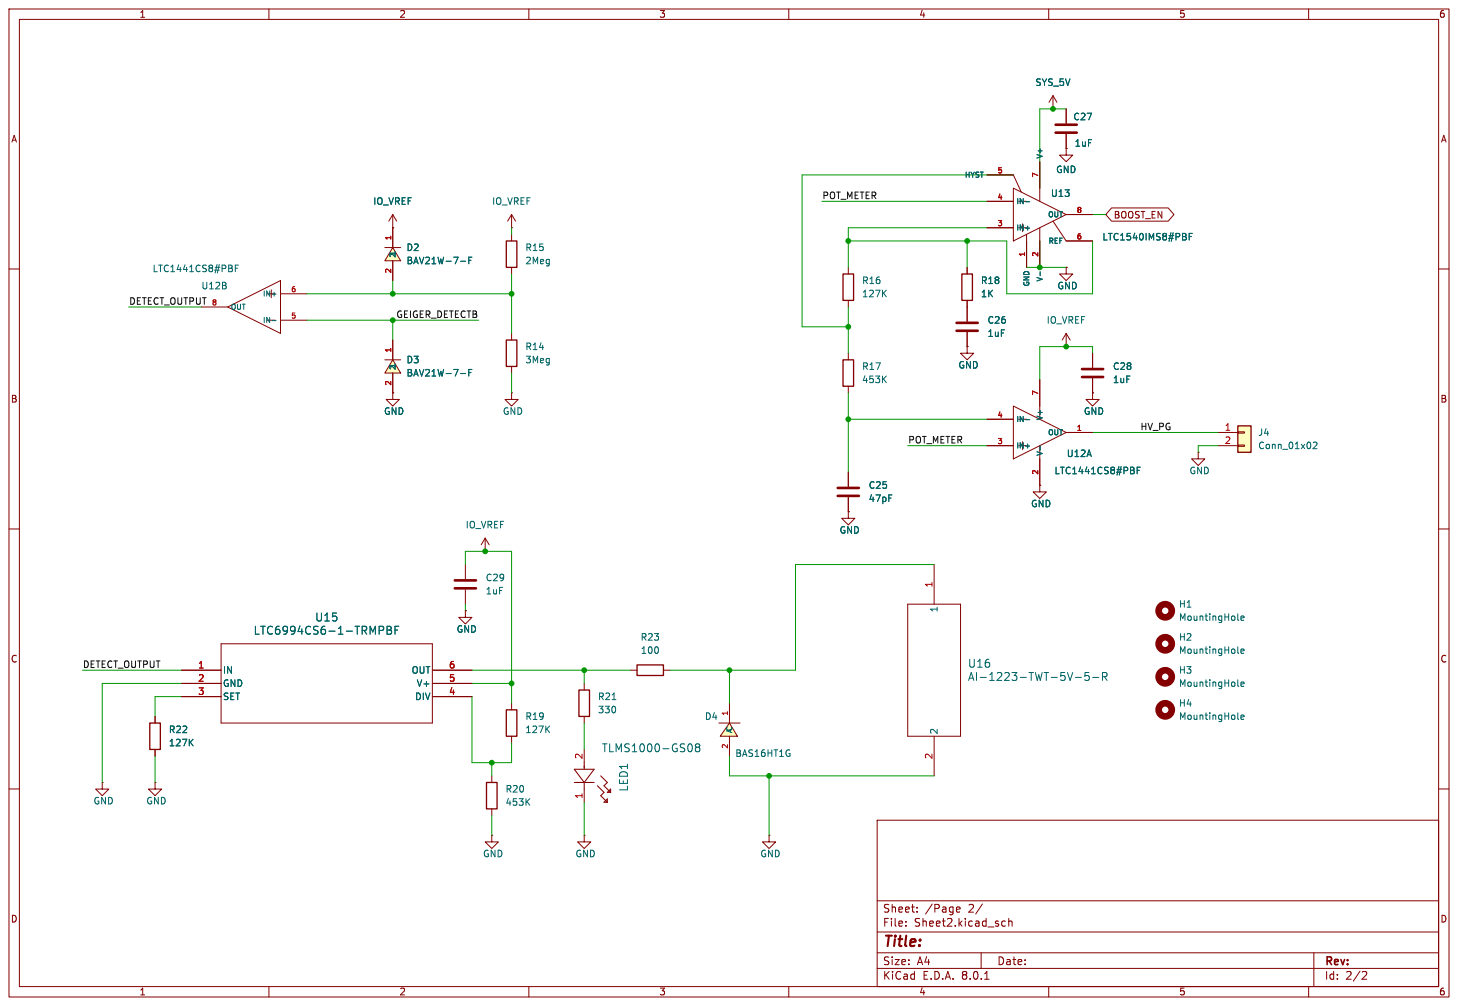
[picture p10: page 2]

Id: 2/2 Title: File: Sheet2.kicad_sch Sheet: /Page 2/

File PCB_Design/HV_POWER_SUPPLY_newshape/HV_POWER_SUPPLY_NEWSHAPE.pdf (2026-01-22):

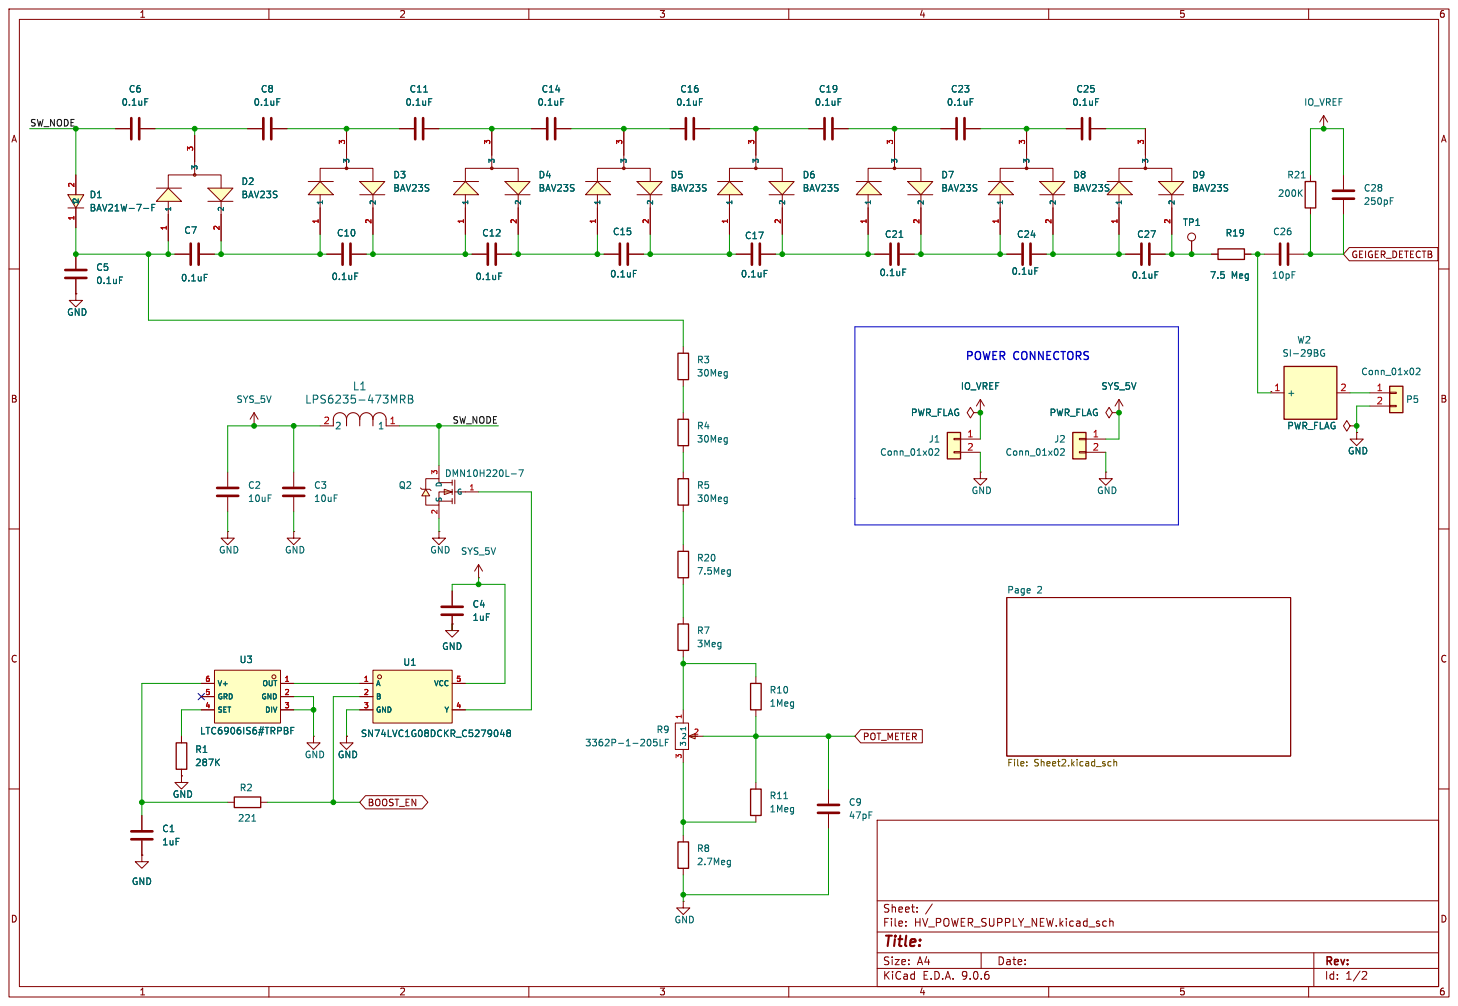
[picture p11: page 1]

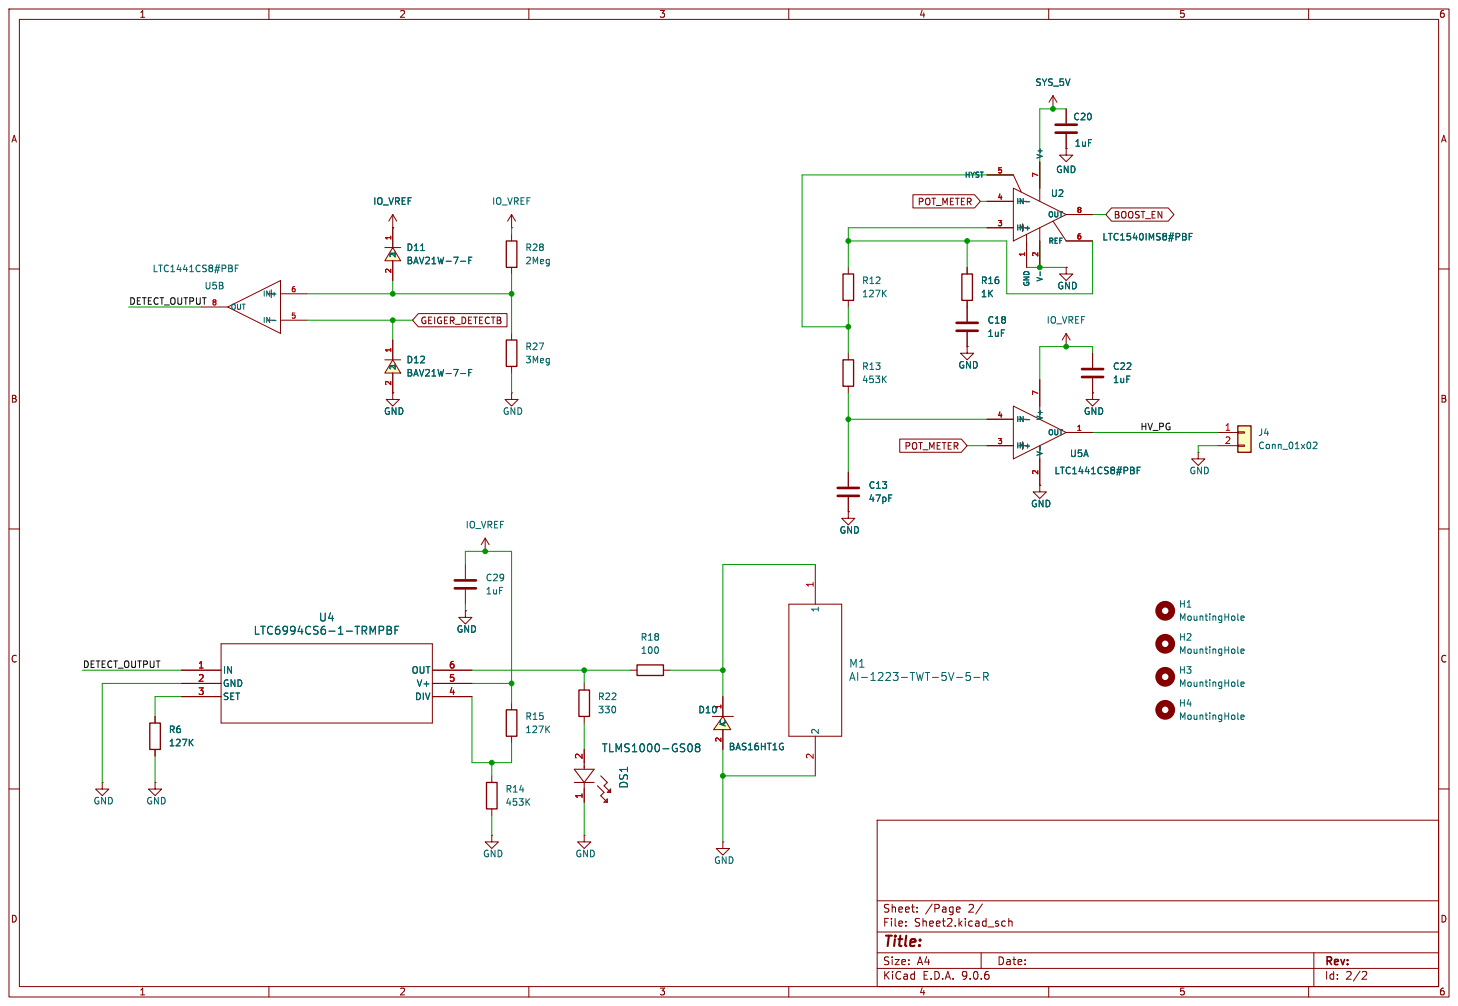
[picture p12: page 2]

Id: 2/2 Title: File: Sheet2.kicad_sch Sheet: /Page 2/

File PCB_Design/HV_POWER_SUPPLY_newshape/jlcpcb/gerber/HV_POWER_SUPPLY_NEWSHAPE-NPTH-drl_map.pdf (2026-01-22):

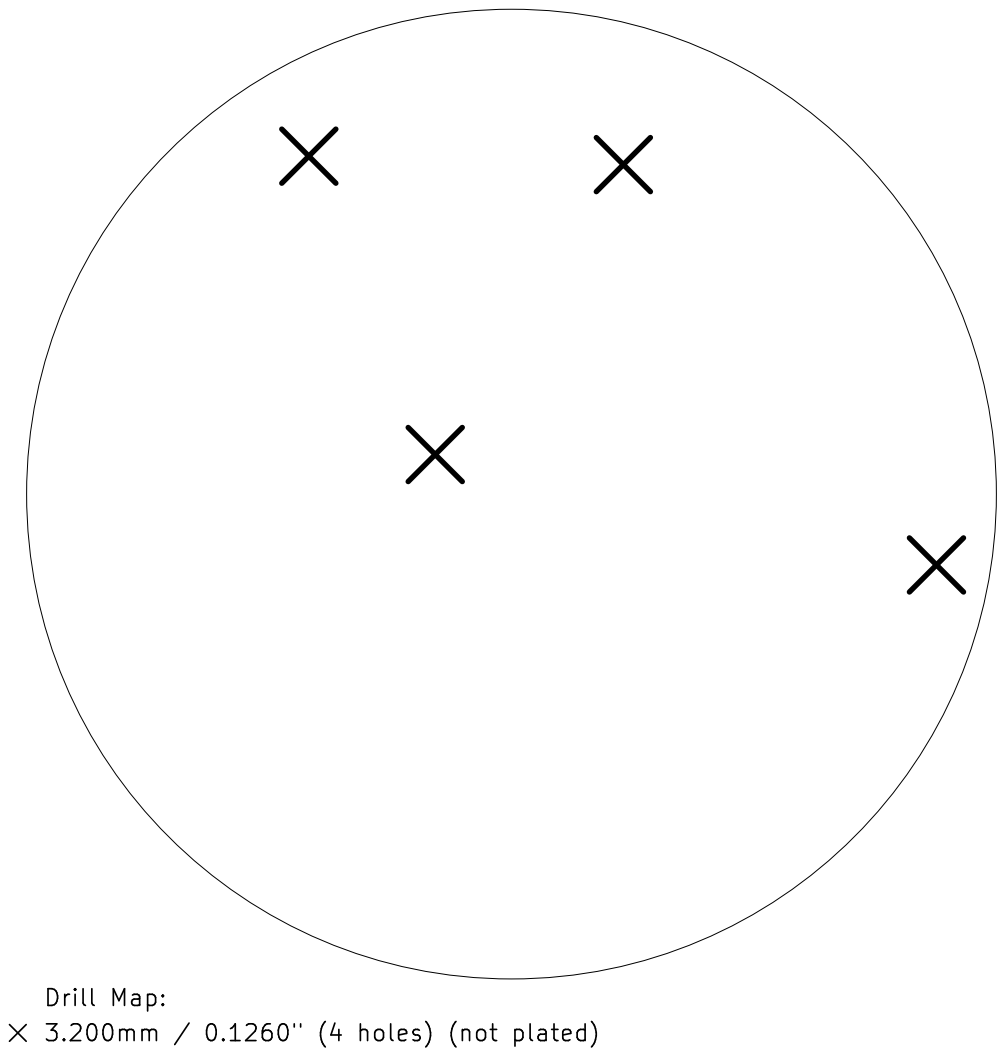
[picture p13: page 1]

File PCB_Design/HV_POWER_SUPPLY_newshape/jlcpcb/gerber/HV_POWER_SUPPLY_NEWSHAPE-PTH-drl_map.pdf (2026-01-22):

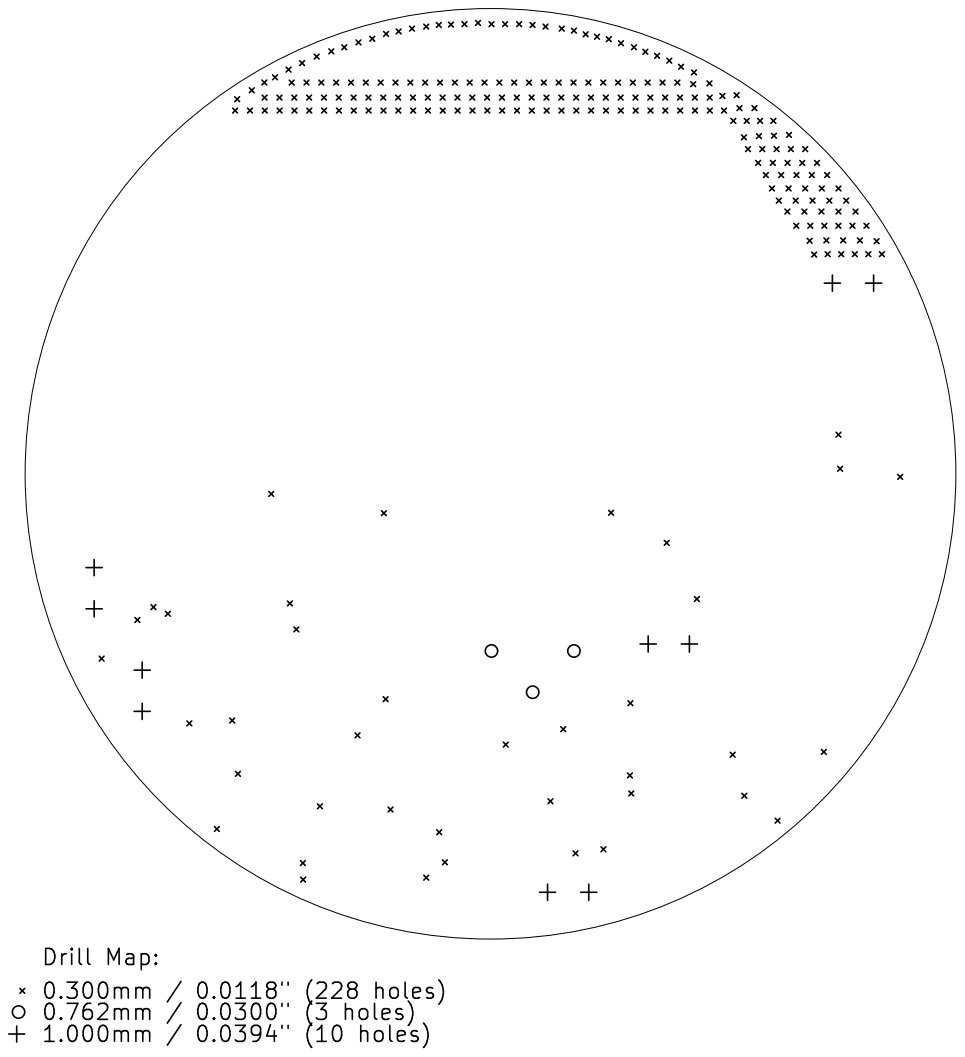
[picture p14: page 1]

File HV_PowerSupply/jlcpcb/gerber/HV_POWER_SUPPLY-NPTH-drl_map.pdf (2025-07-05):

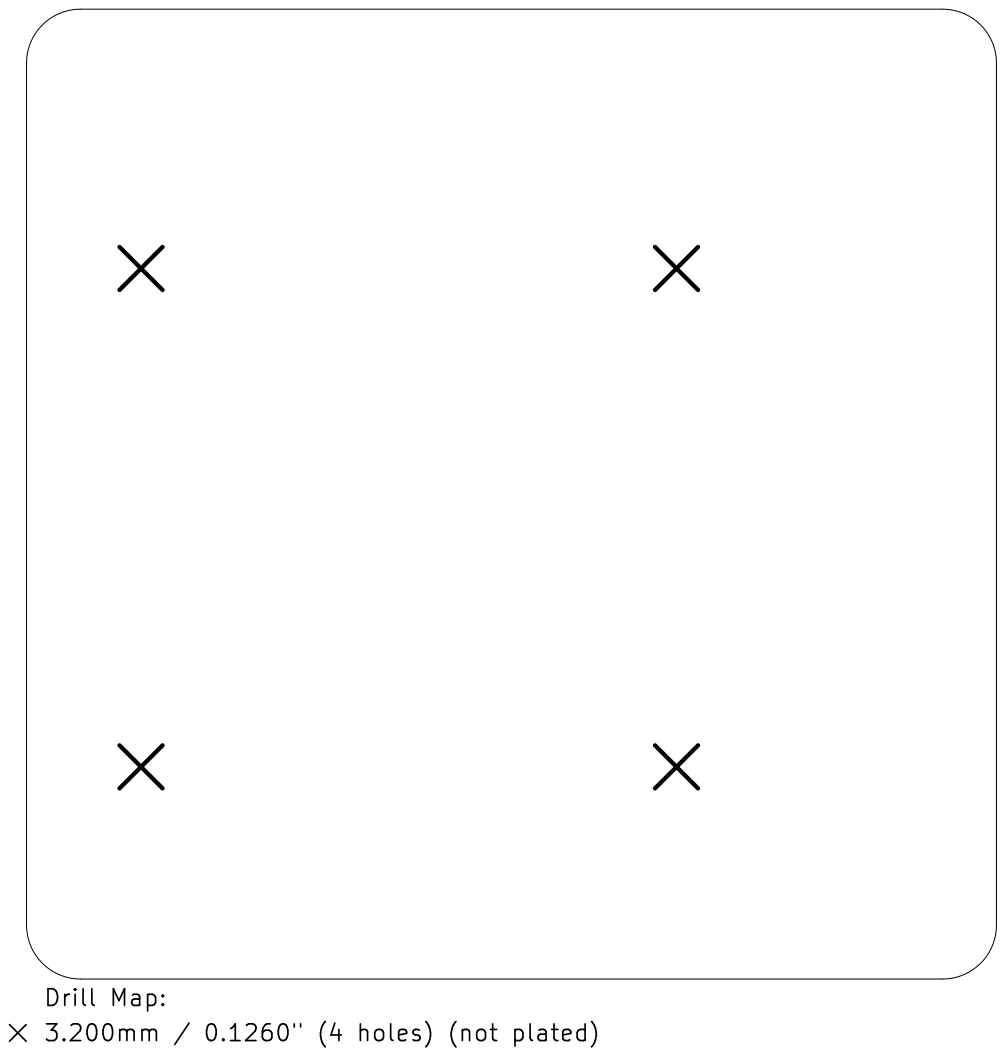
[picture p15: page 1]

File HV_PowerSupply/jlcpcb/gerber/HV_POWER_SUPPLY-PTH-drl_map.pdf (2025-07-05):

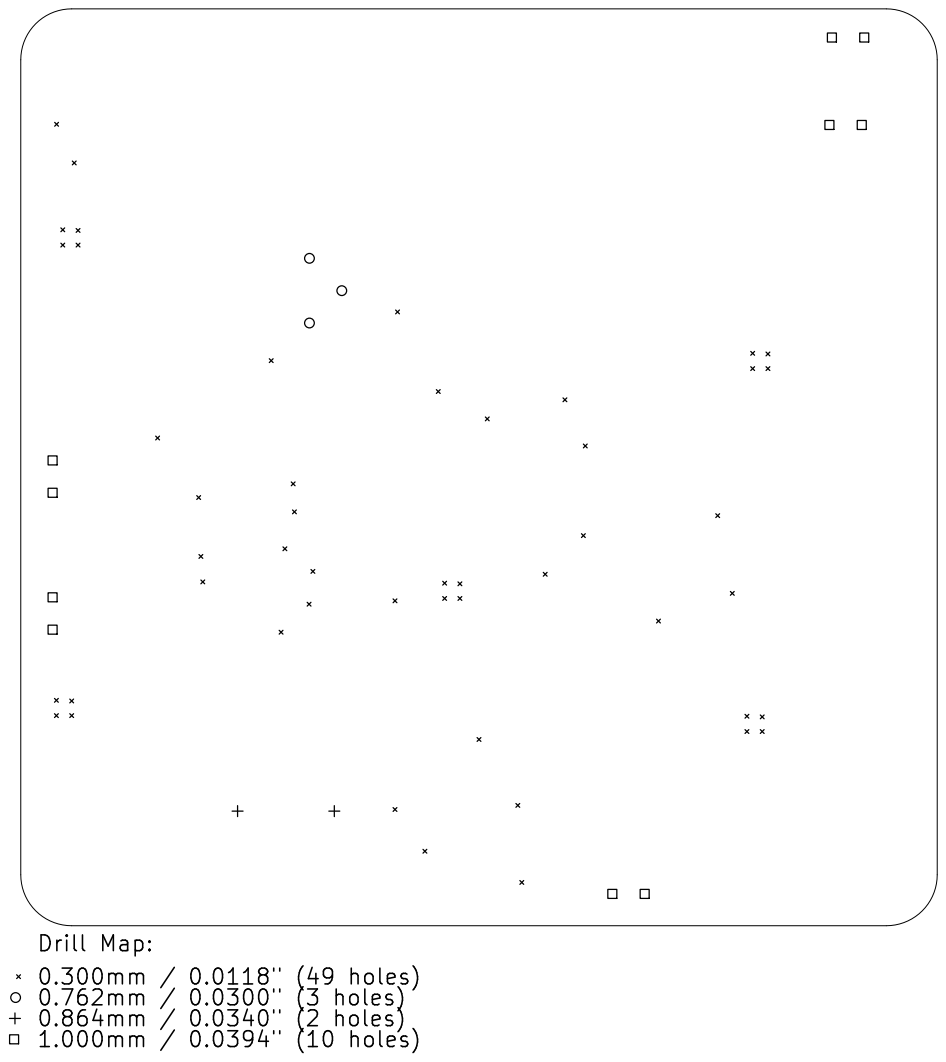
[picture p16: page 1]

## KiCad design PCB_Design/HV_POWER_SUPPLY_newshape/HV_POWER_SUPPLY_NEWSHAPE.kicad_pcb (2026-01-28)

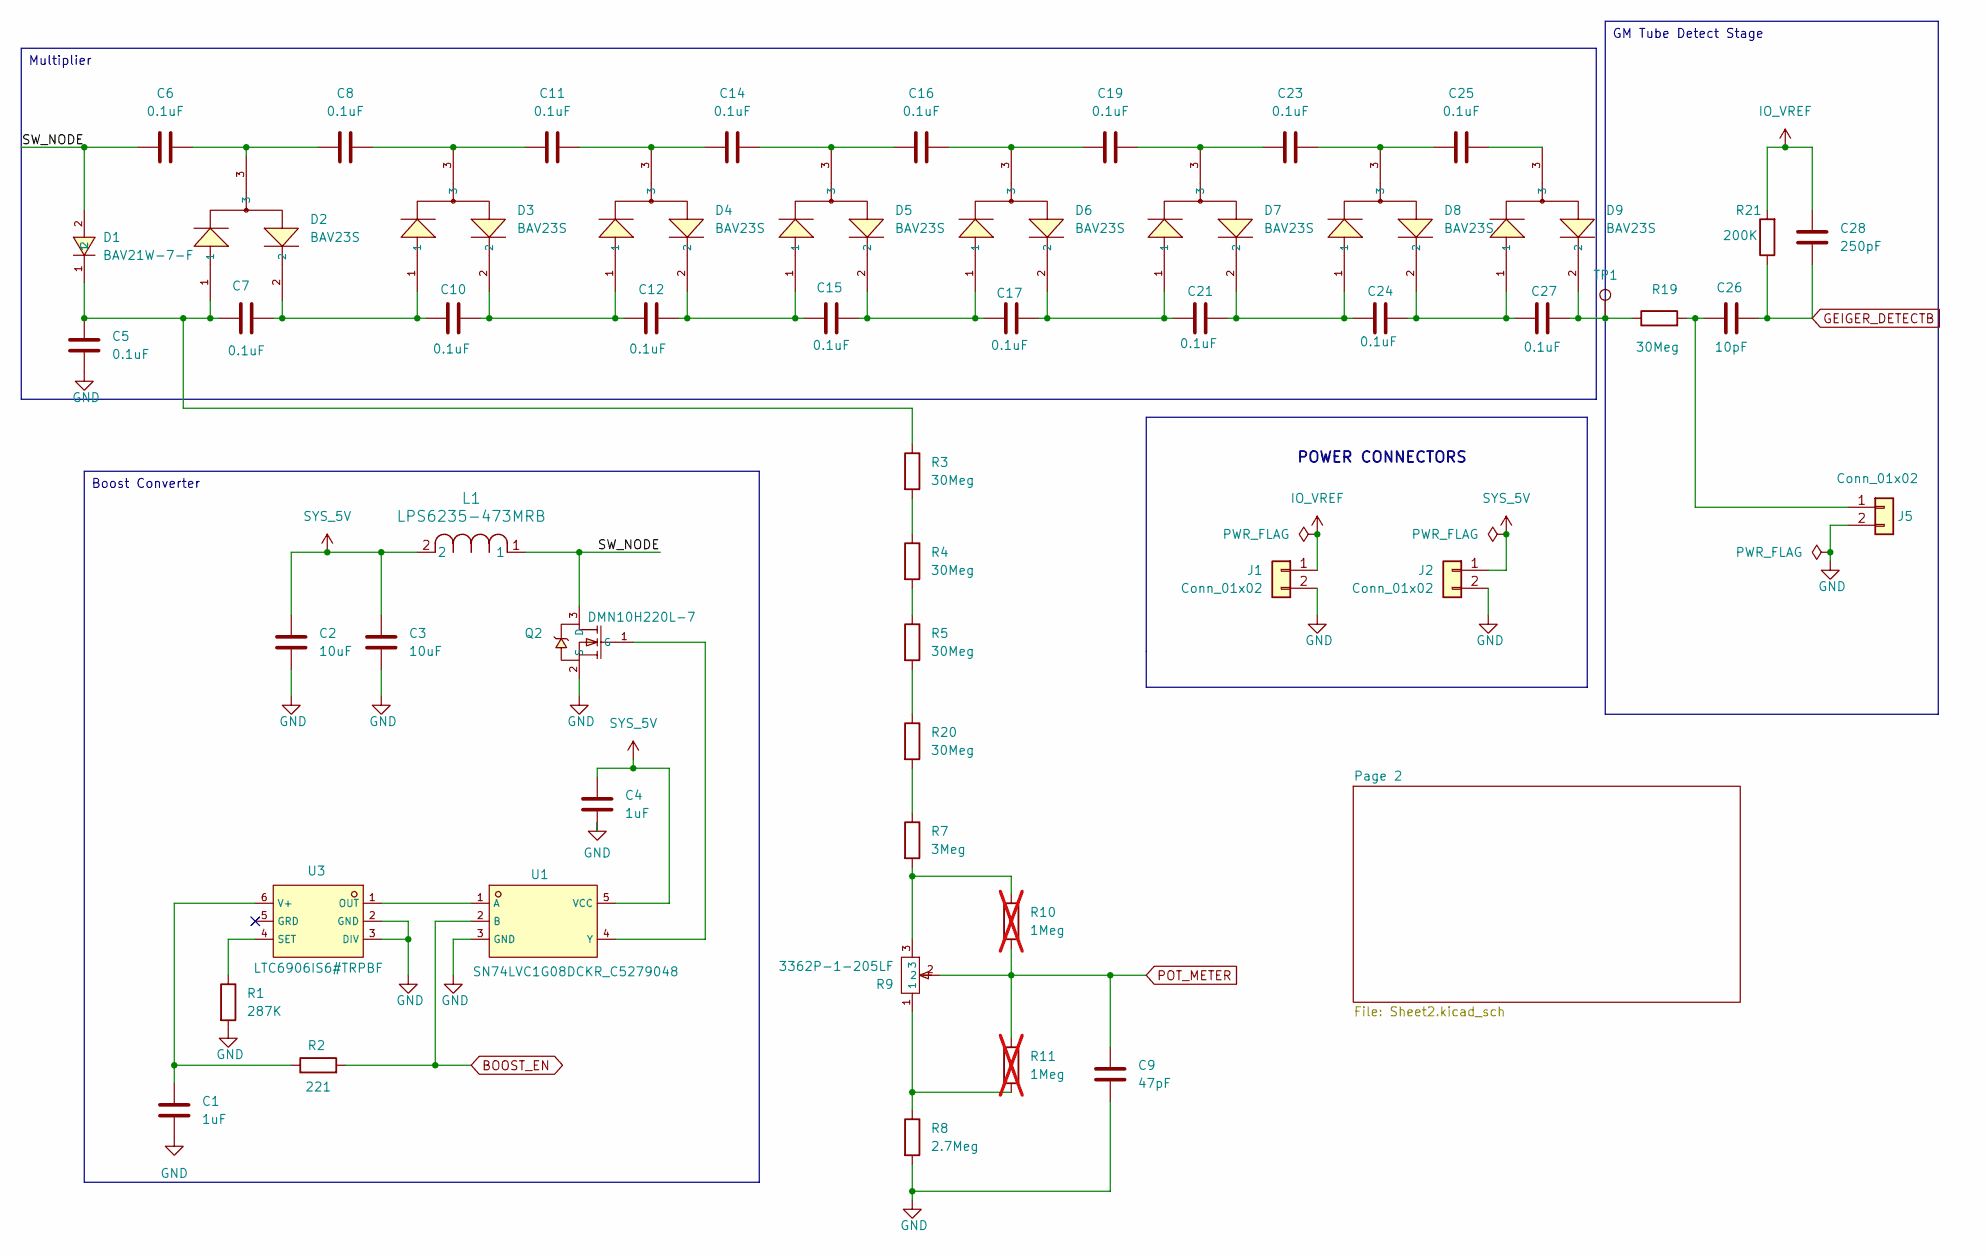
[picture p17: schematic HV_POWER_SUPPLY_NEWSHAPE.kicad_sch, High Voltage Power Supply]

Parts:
C1, C4: 1uF; C_0603_1608Metric; manufacturer Part Number 0603YC105KAT2A; LCSC C4153100
C2, C3: 10uF; C_0805_2012Metric; manufacturer Part Number GRM21BR61C106KE15L; LCSC C77075
C5, C6, C7, C8, C10, C11, C12, C14, C15, C16, C17, C19, C21, C23, C24, C25, C27: 0.1uF; C_1206_3216Metric; manufacturer Part Number 12061C104JAT2A; LCSC C597455
C9: 47pF; C_0603_1608Metric; manufacturer Part Number C0603C470K5RACAUTO; LCSC C2169937
C26: 10pF; C_1206_3216Metric; manufacturer Part Number CGA1206C0G100J102MT; LCSC C22374878
C28: 250pF; C_0603_1608Metric; manufacturer Part Number 06033A251JAT2A; Digikey part number 478-11806-2-ND
D1: BAV21W-7-F; SOD-123_L2.8-W1.8-LS3.7-RD; manufacturer Part Number BAV21WS-7-F; LCSC C155214
D2, D3, D4, D5, D6, D7, D8, D9: BAV23S; BAV23S_SOT-23-3_L2.9-W1.6-P1.90-LS2.8-BR; manufacturer Part Number BAV23S; LCSC C151049
J1, J2, J5: Conn_01x02; PinHeader_1x02_P2.54mm_Vertical; manufacturer Part Number PH1-02-UA; LCSC C5828287
L1: LPS6235-473MRB; LPS6235473MRB; manufacturer Part Number LPS6235-473MRC; Mouser Number 994-LPS6235-473MRB
Q2: DMN10H220L-7; SOT-23-3_L2.9-W1.6-P1.90-LS2.8-BR; manufacturer Part Number DMN10H220L-7; LCSC C102615
R1: 287K; R_0603_1608Metric; manufacturer Part Number RC0603FR-07287KL; LCSC C245944
R2: 221; R_0805_2012Metric; manufacturer Part Number TP0805B221RP0510Z; LCSC C5184183
R3, R4, R5, R19, R20: 30Meg; R_0805_2012Metric; manufacturer Part Number HVCB0805FDC30M0; LCSC HVCB0805FDC30M0
R7: 3Meg; R_0603_1608Metric; manufacturer Part Number CRCW06033M00FKEA; LCSC C4299696
R8: 2.7Meg; R_0603_1608Metric; manufacturer Part Number FRC0805F2704TS; LCSC C403468
R9: 3362P-1-205LF; RES-ADJ-TH_3362P; manufacturer Part Number 3362P-1-205LF; LCSC C124582
R10, R11: 1Meg; R_0603_1608Metric; manufacturer Part Number RC0805FR-071ML; LCSC C107700; not fitted
R21: 200K; R_0603_1608Metric; manufacturer Part Number ERJ3EKF2003V; LCSC C118142
TP1: TestPoint; TestPoint_Pad_1.0x1.0mm
U1: SN74LVC1G08DCKR_C5279048; SC-70-5_L2.0-W1.3-P0.65-LS2.1-BR; manufacturer Part Number SN74LVC1G08DCKR; LCSC C7832
U3: LTC6906IS6#TRPBF; TSOT-23-6_L2.9-W1.6-P0.95-LS2.8-BR; manufacturer Part Number LTC6906IS6#TRMPBF; LCSC C581017

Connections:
/SW_NODE: C6.1, D1.2, L1.1, Q2.3 (D)
BOOST_EN: R2.2, U1.2 (B); also elsewhere on the board
GEIGER_DETECTB: C26.2, C28.1, R21.1; also elsewhere on the board
GND: C1.2, C2.2, C3.2, C4.2, C5.2, C9.2, J1.2, J2.2, J5.2, Q2.2 (S), R1.2, R8.2, U1.3 (GND), U3.2 (GND), U3.3 (DIV); also elsewhere on the board
IO_VREF: C28.2, J1.1, R21.2; also elsewhere on the board
unnamed: C5.1, C7.1, D1.1, D2.1, R3.1
unnamed: C6.2, C8.1, D2.3
unnamed: C7.2, C10.1, D2.2, D3.1
unnamed: C10.2, C12.1, D3.2, D4.1
unnamed: C8.2, C11.1, D3.3
unnamed: C11.2, C14.1, D4.3
unnamed: C12.2, C15.1, D4.2, D5.1
unnamed: C14.2, C16.1, D5.3
unnamed: C15.2, C17.1, D5.2, D6.1
unnamed: C16.2, C19.1, D6.3
unnamed: C17.2, C21.1, D6.2, D7.1
unnamed: C19.2, C23.1, D7.3
unnamed: C21.2, C24.1, D7.2, D8.1
unnamed: C23.2, C25.1, D8.3
unnamed: C24.2, C27.1, D8.2, D9.1
unnamed: C25.2, D9.3
unnamed: C27.2, D9.2, R19.1, TP1.1
unnamed: C26.1, J5.1, R19.2
unnamed: Q2.1 (G), U1.4 (Y)
unnamed: R3.2, R4.1
unnamed: R4.2, R5.1
unnamed: R7.2, R9.3, R10.1
unnamed: R8.1, R9.1, R11.2
unnamed: R5.2, R20.1
unnamed: R7.1, R20.2
unnamed: U1.1 (A), U3.1 (OUT)
unnamed: R1.1, U3.4 (SET)
unnamed: C1.1, R2.1, U3.6 (V+)
POT_METER: C9.1, R9.2, R10.2, R11.1; also elsewhere on the board
SYS_5V: C2.1, C3.1, C4.1, J2.1, L1.2, U1.5 (VCC); also elsewhere on the board

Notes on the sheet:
POWER CONNECTORS
Boost Converter
GM Tube Detect Stage
Multiplier

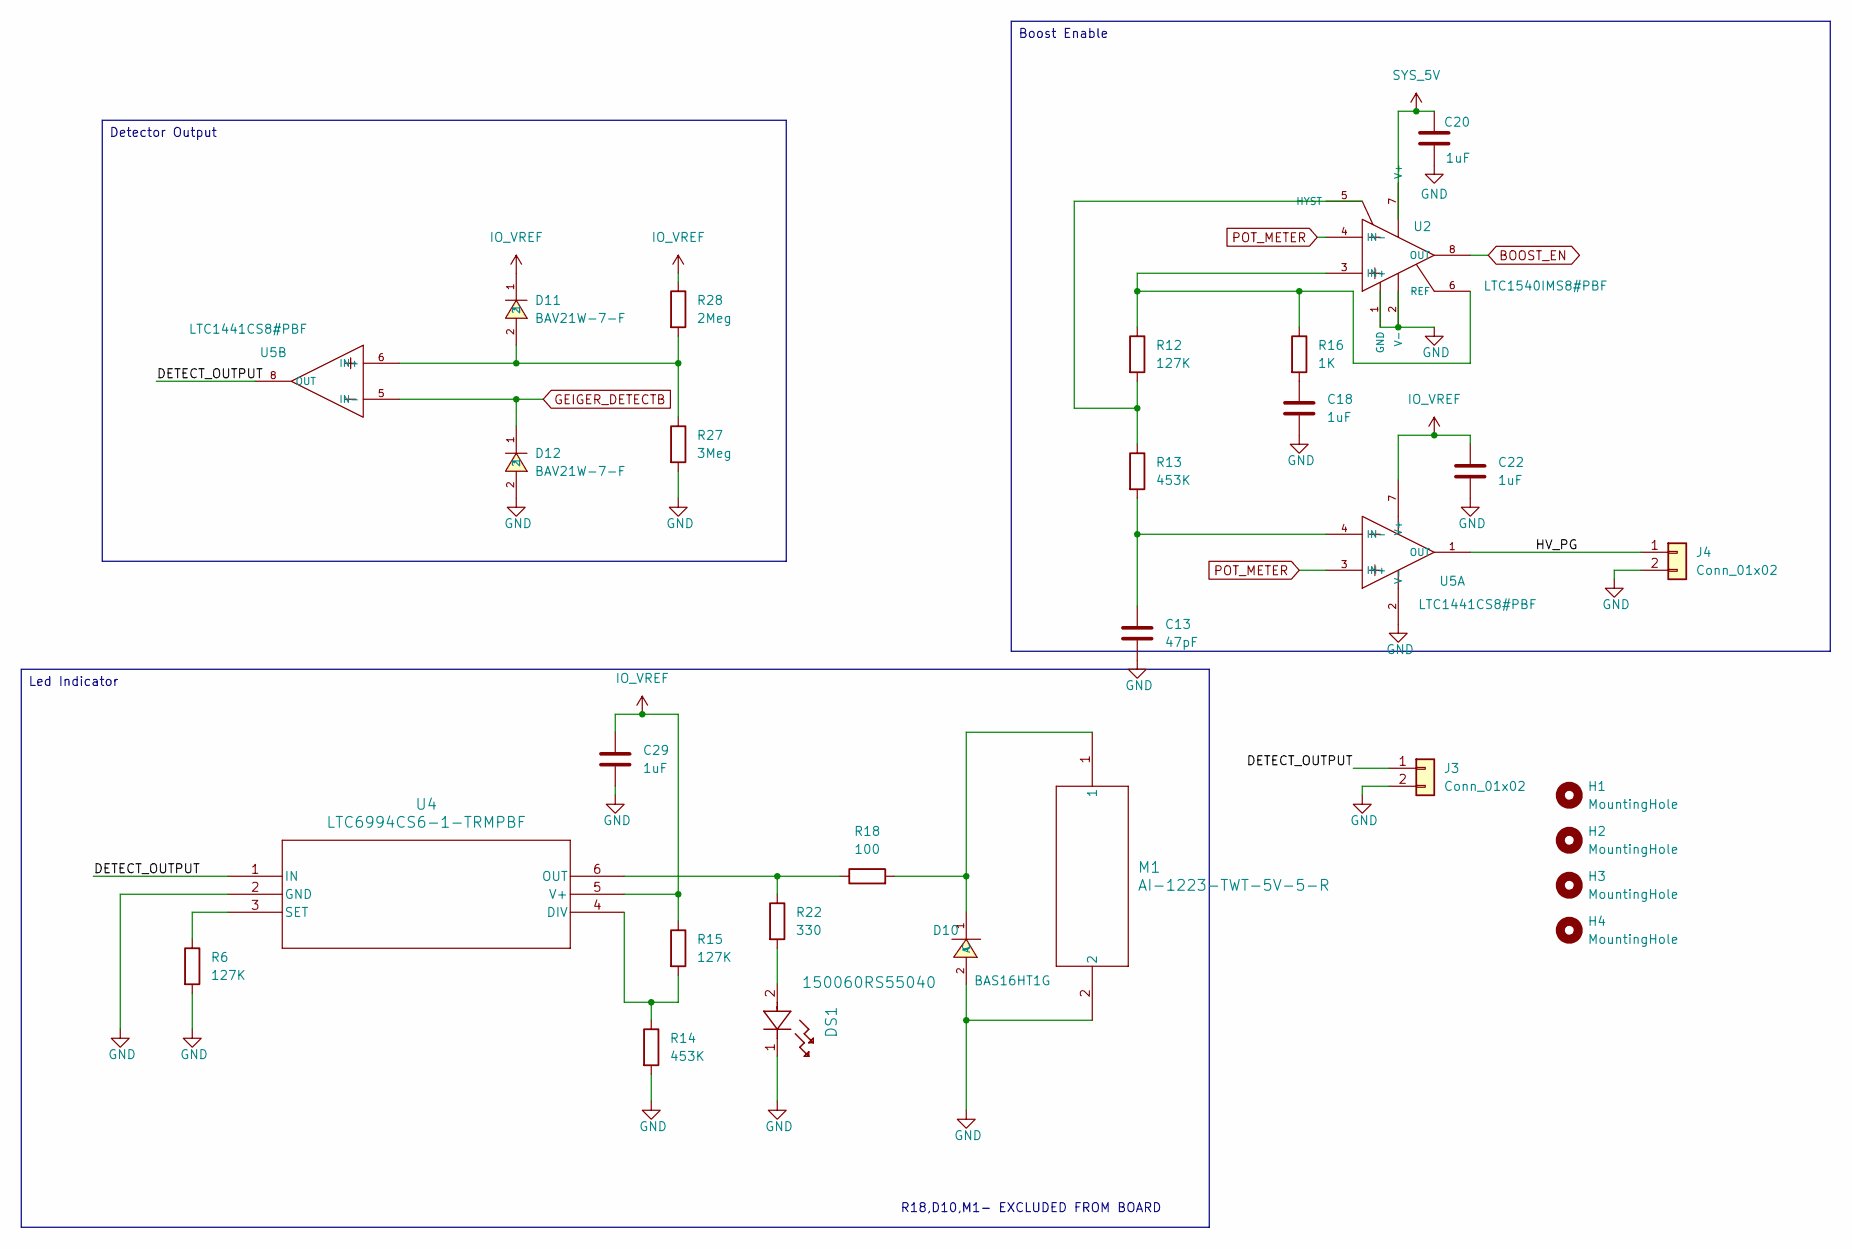
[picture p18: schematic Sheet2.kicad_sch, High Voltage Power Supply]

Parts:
C13: 47pF; C_0603_1608Metric; manufacturer Part Number C0603C470K5RACAUTO; LCSC C2169937
C18, C20, C22, C29: 1uF; C_0603_1608Metric; manufacturer Part Number 0603YC105KAT2A; LCSC C4153100
D10: BAS16HT1G; SOD-323_L1.8-W1.3-LS2.5-RD; manufacturer Part Number BAS16HT1G; LCSC C131148
D11, D12: BAV21W-7-F; SOD-123_L2.8-W1.8-LS3.7-RD; manufacturer Part Number BAV21WS-7-F; LCSC C155214
DS1: 150060RS55040; LED_0603_1608Metric; manufacturer Part Number 150060RS55040; LCSC C6067128
H1, H2, H3, H4: MountingHole; MountingHole_3.2mm_M3
J3, J4: Conn_01x02; PinHeader_1x02_P2.54mm_Vertical; manufacturer Part Number PH1-02-UA; LCSC C5828287
M1: AI-1223-TWT-5V-5-R; AI-1223-TWT-5V-5-R_PUI; manufacturer Part Number AI-1223-TWT-5V-5-R; LCSC C5250722
R6, R12, R15: 127K; R_0603_1608Metric; manufacturer Part Number RC0603FR-07127KL; LCSC C245905
R13, R14: 453K; R_0603_1608Metric; manufacturer Part Number RC0603FR-07453KL; LCSC C273765
R16: 1K; R_0603_1608Metric; manufacturer Part Number RC0603FR-071KL; LCSC C22548
R18: 100; R_0603_1608Metric; manufacturer Part Number 0805W8F1000T5E; LCSC C17408
R22: 330; R_0603_1608Metric; manufacturer Part Number 0603WAJ0331T5E; LCSC C25231
R27: 3Meg; R_0603_1608Metric; manufacturer Part Number CRCW06033M00FKEA; LCSC C4299696
R28: 2Meg; R_0603_1608Metric; manufacturer Part Number RC0603FR-072ML; LCSC C114615
U2: LTC1540IMS8#PBF; MSOP-8_L3.0-W3.0-P0.65-LS4.9-BL; manufacturer Part Number LTC1540IMS8#PBF; LCSC C580397
U4: LTC6994CS6-1-TRMPBF; TSOT-23_S6_LIT; manufacturer Part Number LTC6994CS6-1#TRMPBF; LCSC C581050
U5: LTC1441CS8#PBF; SOIC-8_L4.9-W3.8-P1.27-LS6.0-BL; manufacturer Part Number LTC1441CS8#PBF; LCSC C675522

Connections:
/Page 2/DETECT_OUTPUT: J3.1, U4.1 (IN), U5.8 (OUT)
/Page 2/HV_PG: J4.1, U5.1 (OUT)
BOOST_EN: U2.8 (OUT); also elsewhere on the board
GEIGER_DETECTB: D12.1, U5.5 (IN-); also elsewhere on the board
GND: C13.2, C18.2, C20.2, C22.2, C29.2, D10.2 (A), D12.2, DS1.1, J3.2, J4.2, M1.2, R6.2, R14.2, R27.2, U2.1 (GND), U2.2 (V-), U4.2 (GND), U5.2 (V-); also elsewhere on the board
IO_VREF: C22.1, C29.1, D11.1, R15.1, R28.1, U4.5 (V+), U5.7 (V+); also elsewhere on the board
unnamed: C18.1, R16.2
unnamed: D10.1 (C), M1.1, R18.2
unnamed: DS1.2, R22.2
unnamed: R12.2, R13.1, U2.5 (HYST)
unnamed: R12.1, R16.1, U2.3 (IN+), U2.6 (REF)
unnamed: R14.1, R15.2, U4.4 (DIV)
unnamed: R18.1, R22.1, U4.6 (OUT)
unnamed: R6.1, U4.3 (SET)
unnamed: C13.1, R13.2, U5.4 (IN-)
unnamed: D11.2, R27.1, R28.2, U5.6 (IN+)
POT_METER: U2.4 (IN-), U5.3 (IN+); also elsewhere on the board
SYS_5V: C20.1, U2.7 (V+); also elsewhere on the board

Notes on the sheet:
R18,D10,M1- EXCLUDED FROM BOARD
Detector Output
Boost Enable
Led Indicator

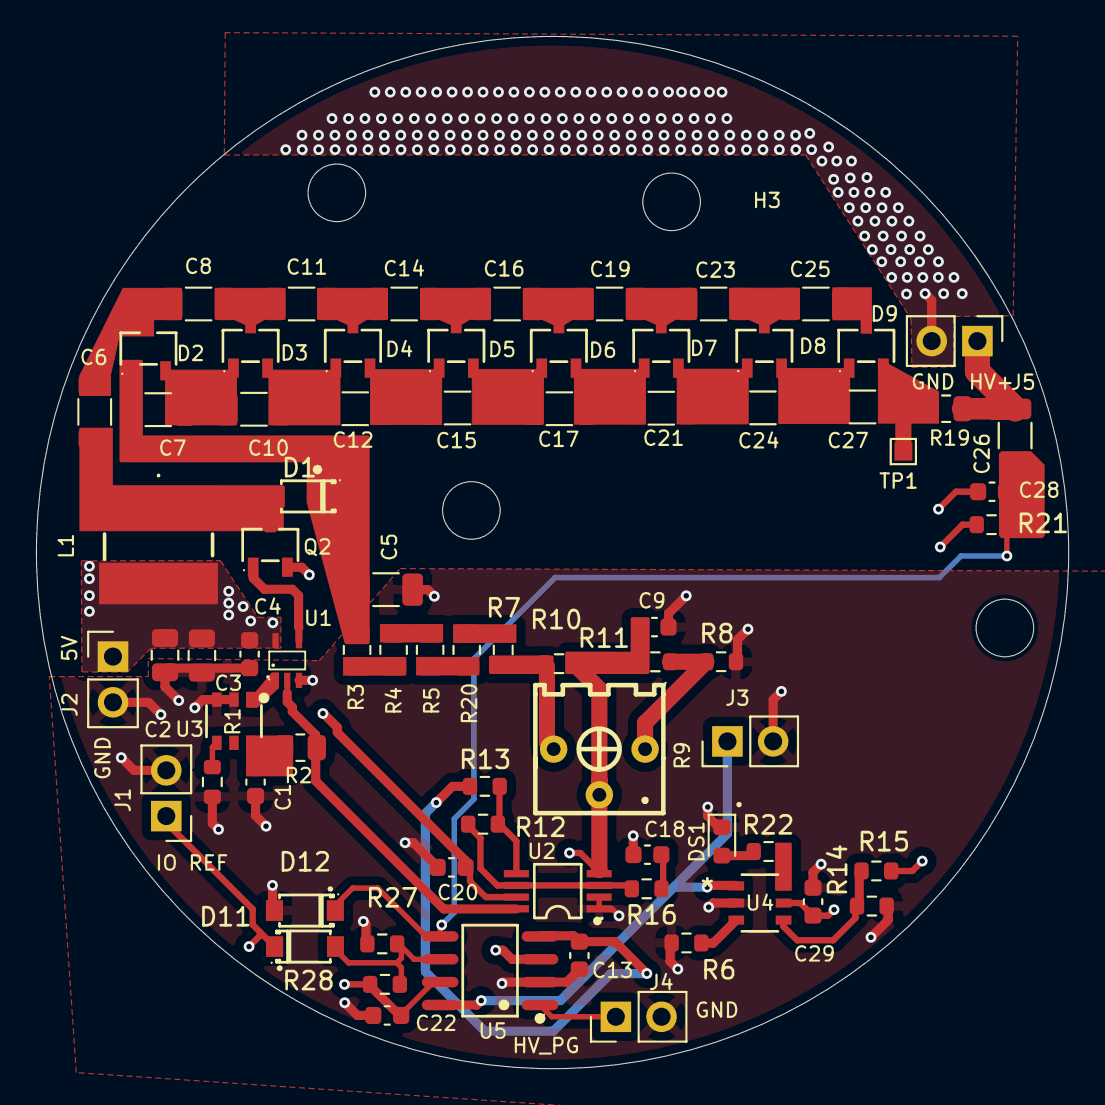
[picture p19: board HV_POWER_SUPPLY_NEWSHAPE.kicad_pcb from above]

Board: 4 copper layers, 57.3 x 57.3 mm, 80 parts (0 on the bottom side), 46 nets.

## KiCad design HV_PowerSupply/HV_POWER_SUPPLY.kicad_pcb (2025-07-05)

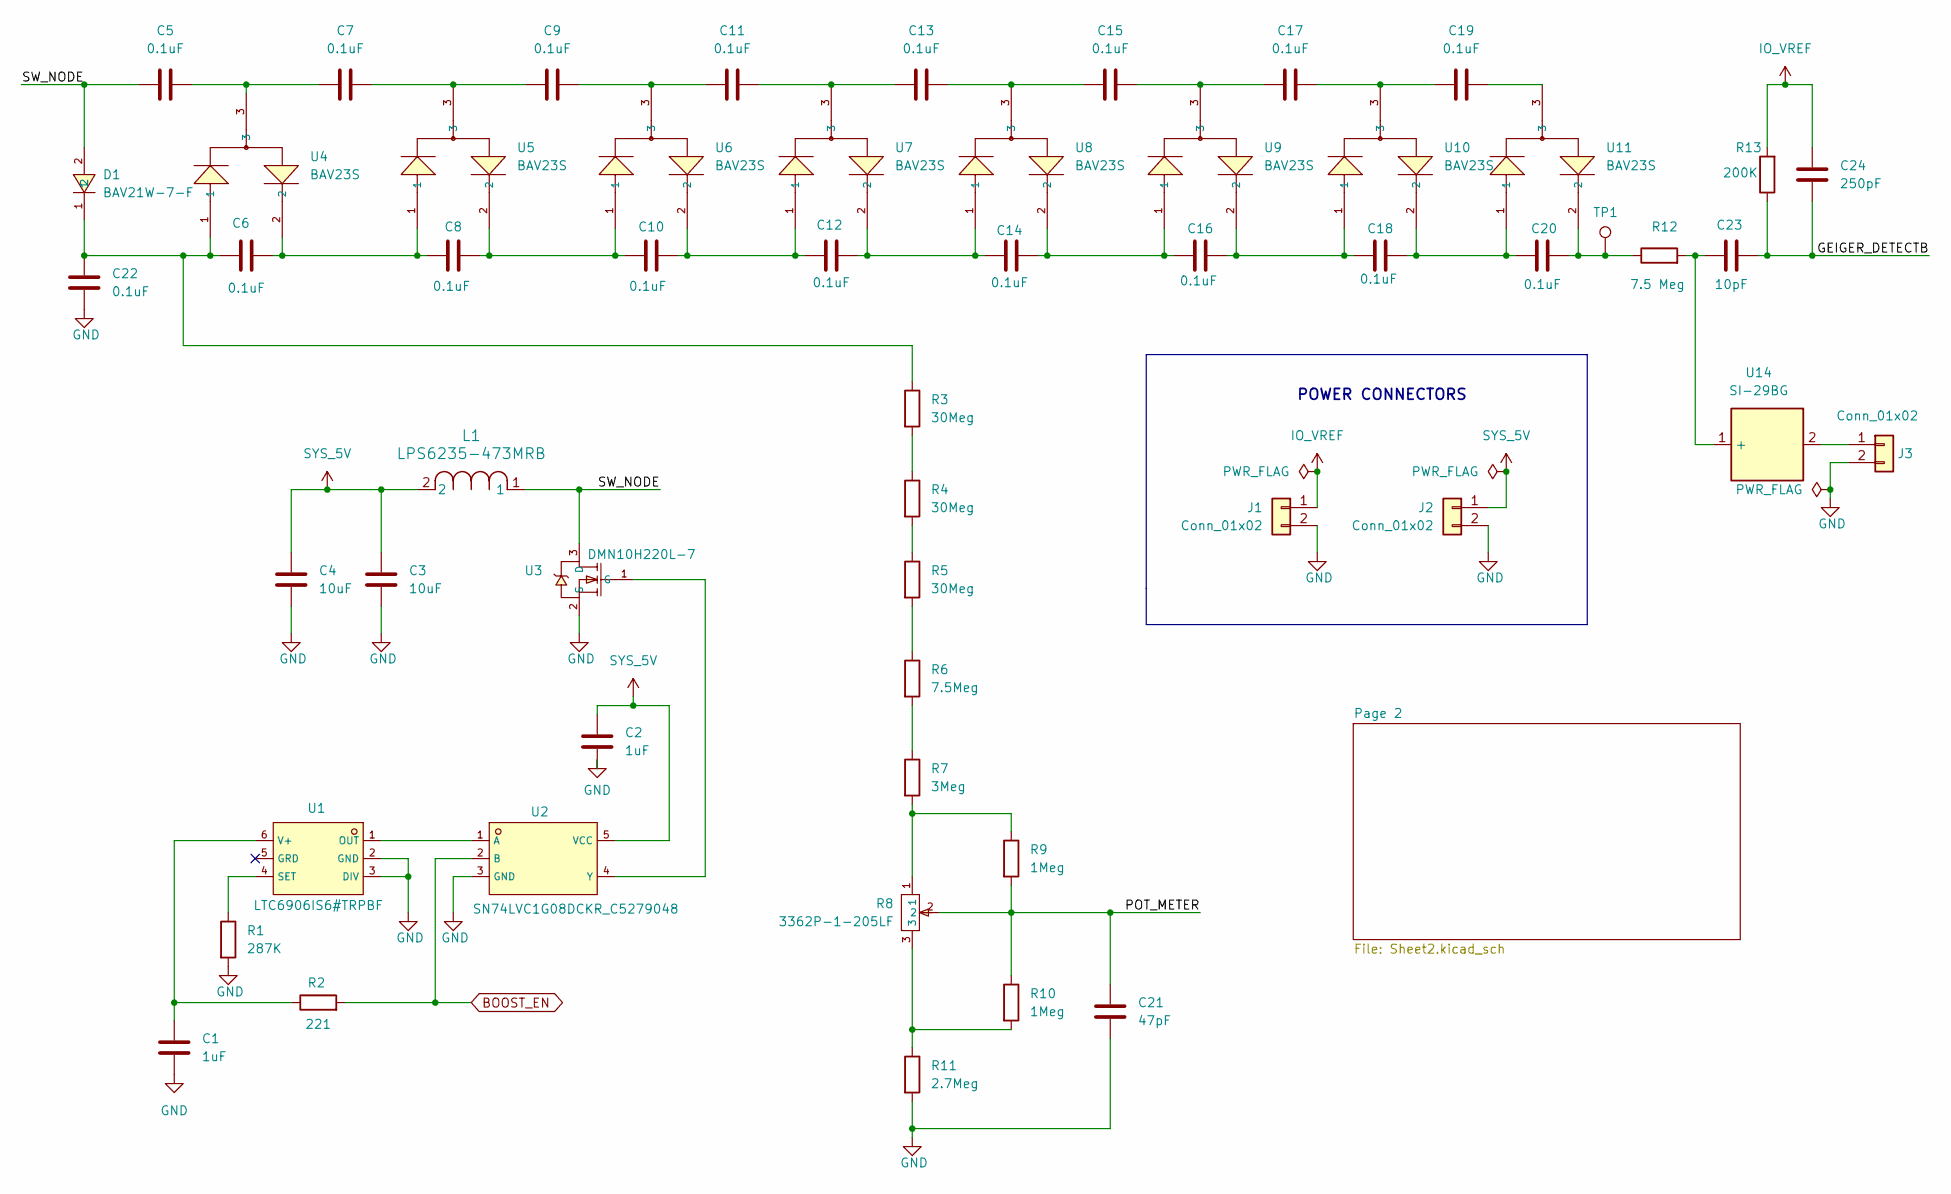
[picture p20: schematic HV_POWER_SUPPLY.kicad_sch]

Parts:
C1, C2: 1uF; C_0603_1608Metric; manufacturer Part Number CL10A105KB8NNNC; LCSC C15849
C3, C4: 10uF; C_0805_2012Metric; manufacturer Part Number CL21A106KAYNNNE; LCSC C15850
C5, C6, C7, C8, C9, C10, C11, C12, C13, C14, C15, C16, C17, C18, C19, C20, C22: 0.1uF; C_1206_3216Metric; manufacturer Part Number CL31B104KBCNNNC; LCSC C24497
C21: 47pF; C_0603_1608Metric; manufacturer Part Number 0603X476M6R3NT; LCSC C178330
C23: 10pF; C_1206_3216Metric; manufacturer Part Number TCC1206COG100J102DT; LCSC C377014
C24: 250pF; C_0603_1608Metric; manufacturer Part Number 06033A251JAT2A; Digikey part number 478-11806-2-ND
D1: BAV21W-7-F; SOD-323_L1.8-W1.3-LS2.5-RD; manufacturer Part Number BAV21WS-7-F; LCSC C151350
J1, J2, J3: Conn_01x02; PinHeader_1x02_P2.54mm_Vertical
L1: LPS6235-473MRB; LPS6235473MRB; manufacturer Part Number LPS6235-473MRB; Mouser Number 994-LPS6235-473MRB
R1: 287K; R_0603_1608Metric; manufacturer Part Number 0603WAF2873T5E; LCSC C22972
R2: 221; R_0805_2012Metric; manufacturer Part Number CR0805-FX-2210ELF; LCSC C204308
R3, R4, R5: 30Meg; R_0805_2012Metric; manufacturer Part Number FHW0805UC2N2KGT; LCSC C317991
R6: 7.5Meg; R_0805_2012Metric; manufacturer Part Number FRC0805J755 TS; LCSC C2933569
R7: 3Meg; R_0805_2012Metric; manufacturer Part Number FRC0805J305 TS; LCSC C2907325
R8: 3362P-1-205LF; RES-ADJ-TH_3362P; manufacturer Part Number 3362P-1-205LF; LCSC C124582
R9, R10: 1Meg; R_0805_2012Metric; manufacturer Part Number RC0805FR-071ML; LCSC C107700
R11: 2.7Meg; R_0805_2012Metric; manufacturer Part Number FRC0805F2704TS; LCSC C2933390
R12: 7.5 Meg; R_0805_2012Metric; manufacturer Part Number FRC0805J755 TS; LCSC C2933569
R13: 200K; R_0805_2012Metric; manufacturer Part Number 0805W8F2003T5E; LCSC C17539
TP1: TestPoint; TestPoint_Pad_1.0x1.0mm
U1: LTC6906IS6#TRPBF; TSOT-23-6_L2.9-W1.6-P0.95-LS2.8-BR; manufacturer Part Number LTC6906IS6#TRPBF; LCSC C689638
U2: SN74LVC1G08DCKR_C5279048; SC-70-5_L2.0-W1.3-P0.65-LS2.1-BR; manufacturer Part Number SN74LVC1G08DCKR; LCSC C5279048
U3: DMN10H220L-7; SOT-23-3_L2.9-W1.6-P1.90-LS2.8-BR; manufacturer Part Number DMN10H220L-7; LCSC C102615
U4, U5, U6, U7, U8, U9, U10, U11: BAV23S; BAV23S_SOT-23-3_L2.9-W1.6-P1.90-LS2.8-BR; manufacturer Part Number BAV23S; LCSC C44345
U14: SI-29BG

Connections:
/GEIGER_DETECTB: C23.2, C24.1, R13.1
/POT_METER: C21.1, R8.2, R9.2, R10.1
/SW_NODE: C5.1, D1.2, L1.1, U3.3 (D)
BOOST_EN: R2.2, U2.2 (B); also elsewhere on the board
GND: C1.2, C2.2, C3.2, C4.2, C21.2, C22.2, J1.2, J2.2, J3.2, R1.2, R11.2, U1.2 (GND), U1.3 (DIV), U2.3 (GND), U3.2 (S); also elsewhere on the board
IO_VREF: C24.2, J1.1, R13.2; also elsewhere on the board
unnamed: C5.2, C7.1, U4.3
unnamed: C6.2, C8.1, U4.2, U5.1
unnamed: C7.2, C9.1, U5.3
unnamed: C8.2, C10.1, U5.2, U6.1
unnamed: C10.2, C12.1, U6.2, U7.1
unnamed: C9.2, C11.1, U6.3
unnamed: C11.2, C13.1, U7.3
unnamed: C12.2, C14.1, U7.2, U8.1
unnamed: C13.2, C15.1, U8.3
unnamed: C14.2, C16.1, U8.2, U9.1
unnamed: C15.2, C17.1, U9.3
unnamed: C16.2, C18.1, U9.2, U10.1
unnamed: C17.2, C19.1, U10.3
unnamed: C18.2, C20.1, U10.2, U11.1
unnamed: C19.2, U11.3
unnamed: C20.2, R12.1, TP1.1, U11.2
unnamed: C6.1, C22.1, D1.1, R3.1, U4.1
unnamed: J3.1, U14.2
unnamed: R3.2, R4.1
unnamed: R4.2, R5.1
unnamed: R5.2, R6.1
unnamed: R6.2, R7.1
unnamed: R7.2, R8.1, R9.1
unnamed: R8.3, R10.2, R11.1
unnamed: U1.1 (OUT), U2.1 (A)
unnamed: R1.1, U1.4 (SET)
unnamed: C1.1, R2.1, U1.6 (V+)
unnamed: U2.4 (Y), U3.1 (G)
unnamed: C23.1, R12.2, U14.1 (+)
SYS_5V: C2.1, C3.1, C4.1, J2.1, L1.2, U2.5 (VCC); also elsewhere on the board

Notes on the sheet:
POWER CONNECTORS

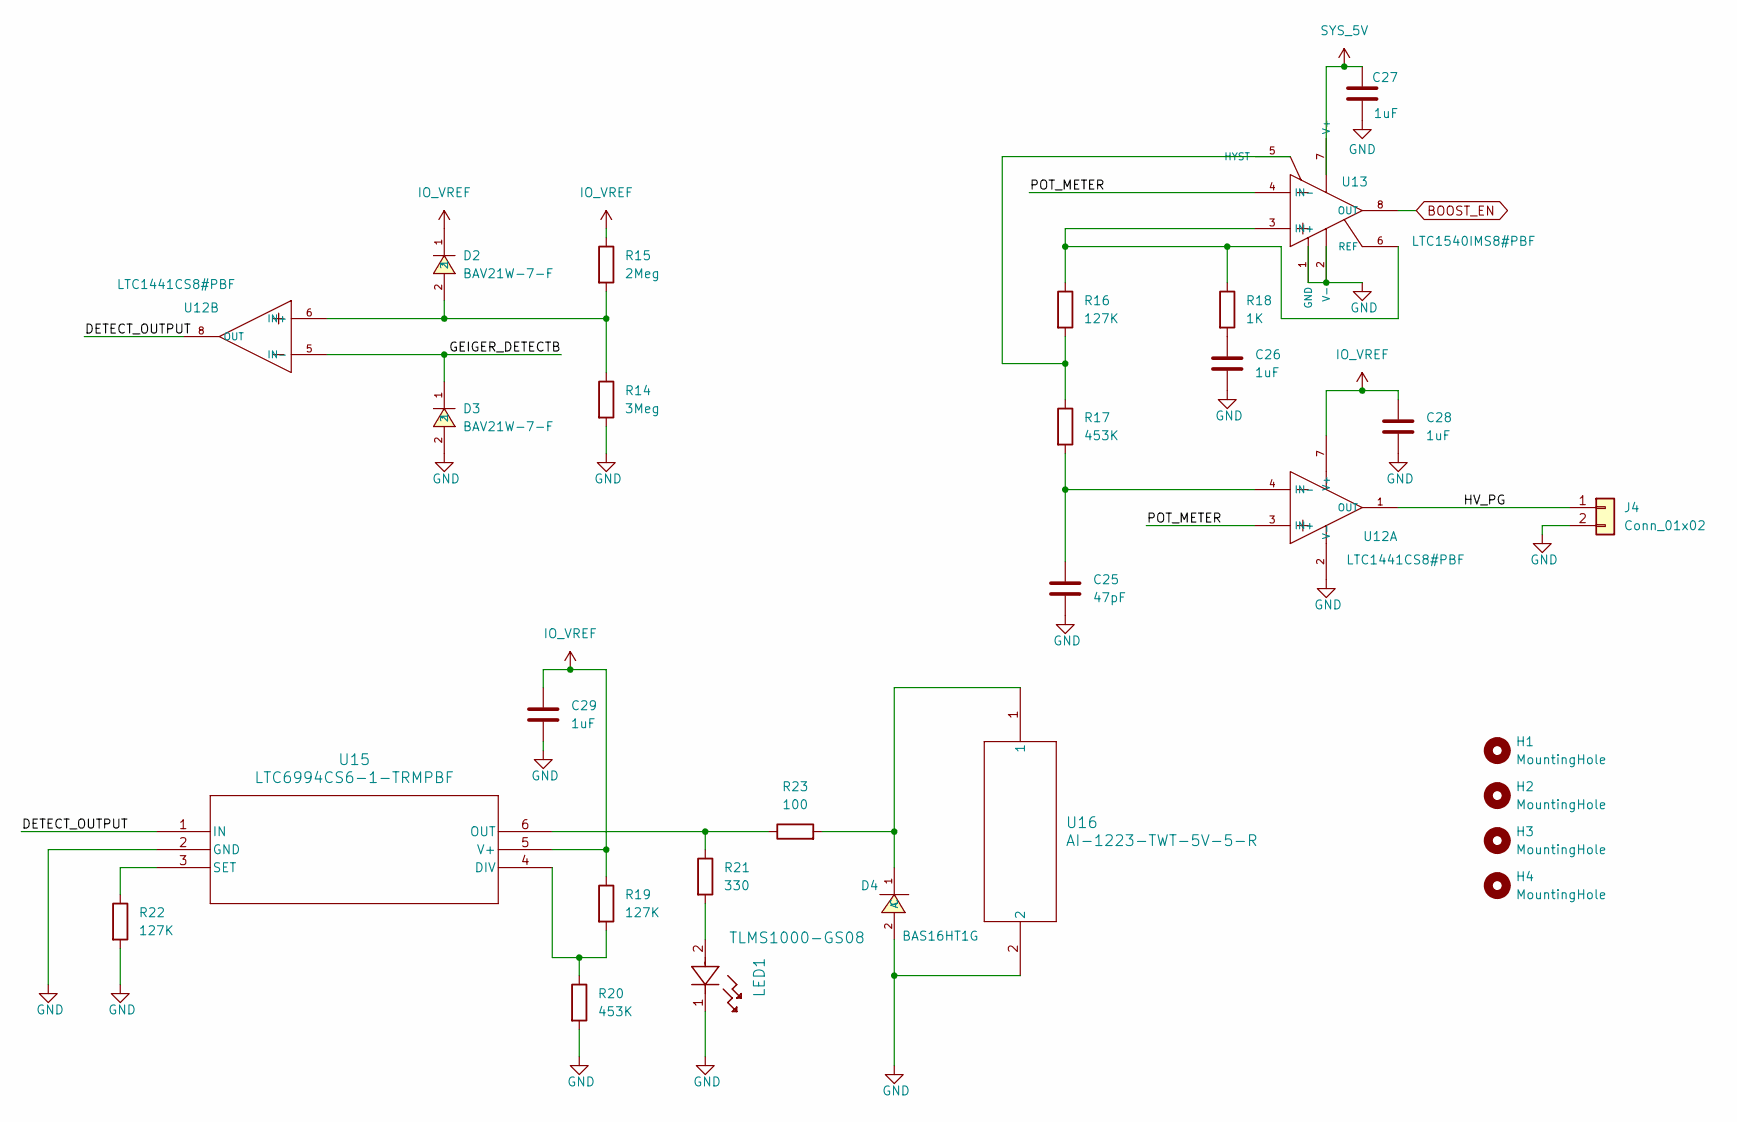
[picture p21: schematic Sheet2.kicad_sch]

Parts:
C25: 47pF; C_0603_1608Metric; manufacturer Part Number 0603X476M6R3NT; LCSC C178330
C26, C27, C28, C29: 1uF; C_0603_1608Metric; manufacturer Part Number CL10A105KB8NNNC; LCSC C15849
D2, D3: BAV21W-7-F; SOD-323_L1.8-W1.3-LS2.5-RD; manufacturer Part Number BAV21WS-7-F; LCSC C151350
D4: BAS16HT1G; SOD-323_L1.8-W1.3-LS2.5-RD; manufacturer Part Number BAS16HT1G; LCSC C131148
H1, H2, H3, H4: MountingHole; MountingHole_3.2mm_M3
J4: Conn_01x02; PinHeader_1x02_P2.54mm_Vertical
LED1: TLMS1000-GS08; LED_0603_1608Metric; manufacturer Part Number KT-0603R; LCSC C2286
R14: 3Meg; R_0805_2012Metric; manufacturer Part Number FRC0805J305 TS; LCSC C2907325
R15: 2Meg; R_0805_2012Metric; manufacturer Part Number 0805W8F2004T5E; LCSC C26112
R16, R19, R22: 127K; R_0805_2012Metric; manufacturer Part Number AC0805FR-07127KL; LCSC C228282
R17, R20: 453K; R_0805_2012Metric; manufacturer Part Number UNI-ROYAL(Uniroyal Elec); LCSC C17702
R18: 1K; R_0805_2012Metric; manufacturer Part Number RC0805JR-071KL; LCSC C100046
R21: 330; R_0805_2012Metric; manufacturer Part Number 0805W8F3300T5E; LCSC C17630
R23: 100; R_0805_2012Metric; manufacturer Part Number 0805W8F1000T5E; LCSC C17408
U12: LTC1441CS8#PBF; SOIC-8_L4.9-W3.8-P1.27-LS6.0-BL; manufacturer Part Number LTC1441CS8#PBF; LCSC C675522
U13: LTC1540IMS8#PBF; MSOP-8_L3.0-W3.0-P0.65-LS4.9-BL; manufacturer Part Number LTC1540IMS8#PBF; LCSC C580397
U15: LTC6994CS6-1-TRMPBF; TSOT-23_S6_LIT; manufacturer Part Number LTC6994CS6-1#TRMPBF; LCSC C581050
U16: AI-1223-TWT-5V-5-R; AI-1223-TWT-5V-5-R_PUI; manufacturer Part Number AI-1223-TWT-5V-5-R; LCSC C5250722

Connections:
/Page 2/DETECT_OUTPUT: U12.8 (OUT), U15.1 (IN)
/Page 2/GEIGER_DETECTB: D3.1, U12.5 (IN-)
/Page 2/HV_PG: J4.1, U12.1 (OUT)
/Page 2/POT_METER: U12.3 (IN+), U13.4 (IN-)
BOOST_EN: U13.8 (OUT); also elsewhere on the board
GND: C25.2, C26.2, C27.2, C28.2, C29.2, D3.2, D4.2 (A), J4.2, LED1.1, R14.2, R20.2, R22.2, U12.2 (V-), U13.1 (GND), U13.2 (V-), U15.2 (GND), U16.2; also elsewhere on the board
IO_VREF: C28.1, C29.1, D2.1, R15.1, R19.1, U12.7 (V+), U15.5 (V+); also elsewhere on the board
unnamed: C26.1, R18.2
unnamed: D4.1 (C), R23.2, U16.1
unnamed: LED1.2, R21.2
unnamed: C25.1, R17.2, U12.4 (IN-)
unnamed: D2.2, R14.1, R15.2, U12.6 (IN+)
unnamed: R16.2, R17.1, U13.5 (HYST)
unnamed: R16.1, R18.1, U13.3 (IN+), U13.6 (REF)
unnamed: R19.2, R20.1, U15.4 (DIV)
unnamed: R21.1, R23.1, U15.6 (OUT)
unnamed: R22.1, U15.3 (SET)
SYS_5V: C27.1, U13.7 (V+); also elsewhere on the board

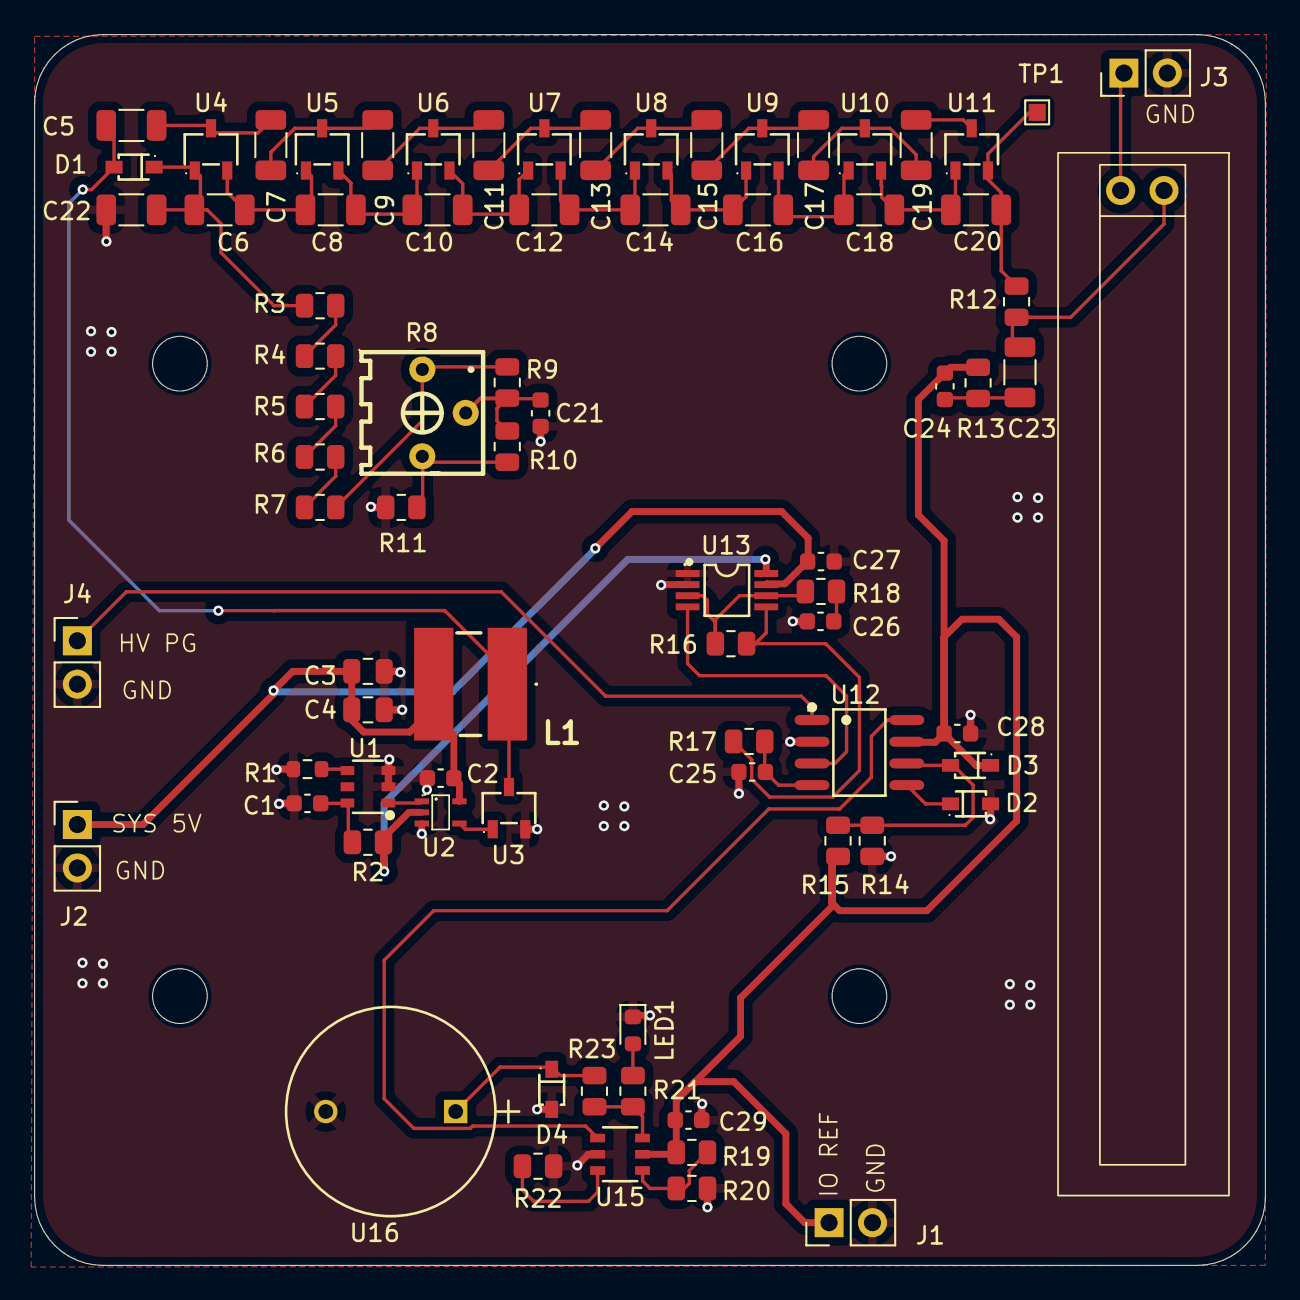
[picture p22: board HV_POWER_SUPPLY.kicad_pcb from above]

Board: 2 copper layers, 72.0 x 72.0 mm, 83 parts (0 on the bottom side), 50 nets.

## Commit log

2025-07-05 Files uploaded
    [BOM-HV_POWER_SUPPLY.csv, CN0536 Allegro File.brd, CN0536 BOM.csv, CPL-HV_POWER_SUPPLY.csv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]
2025-07-05 Into the folder
    [BOM-HV_POWER_SUPPLY.csv, CN0536 Allegro File.brd, CN0536 BOM.csv, CPL-HV_POWER_SUPPLY.csv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]
2026-01-22 ANalog device based design folder added
    [BOM-HV_POWER_SUPPLY_NEWSHAPE.csv, BOM.xls, BOMLCSC.xls, BOMPCBWAY.xls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]
2026-01-22 high voltage board
    [BOM-HV_POWER_SUPPLY_NEWSHAPE.csv, BOM.xls, BOMLCSC.xls, BOMPCBWAY.xls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]
2026-01-23 Added Analog device assets
    [CN0536 Allegro File.brd, CN0536 BOM.csv, ncdrill-1-4.drl]
2026-01-24 -Zone clearance =.5 -added via for SYS_5V -adjust ground via
    [HV_POWER_SUPPLY_NEWSHAPE.kicad_pcb, HV_POWER_SUPPLY_NEWSHAPE.kicad_sch, Sheet2.kicad_sch]
